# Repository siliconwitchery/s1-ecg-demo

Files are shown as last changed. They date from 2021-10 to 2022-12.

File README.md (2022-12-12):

# S1 ECG Reference Kit

**Features:**

- Single chip frontend based on the [AD8233](https://www.analog.com/en/products/ad8233.html)
- S1 Module with Bluetooth 5.2 and FPGA
- Integrated lithium battery
- Ultra low power auto-sleep down to 175uA
- Open source design

**Applications:**

- Learning and teaching around heart health
- Research of ML based ECG algorithms
- Wireless ECG data logging
- New product development

A powerful analog frontend combined with the S1 Module makes this an all-in-one kit to deploy and test algorithms with ease. Be that for learning, research, or as the starting point for your next product.

<br>

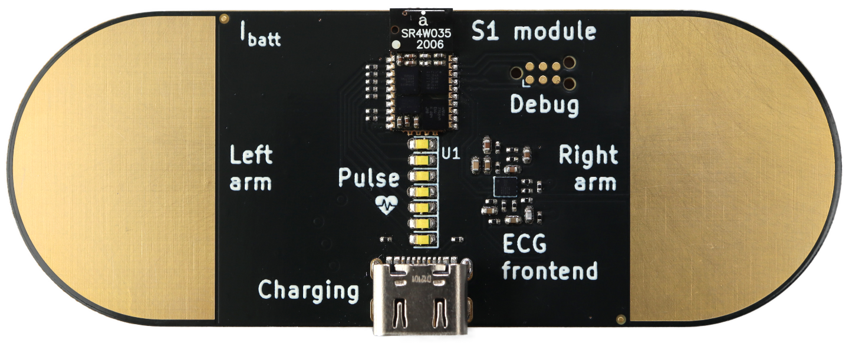
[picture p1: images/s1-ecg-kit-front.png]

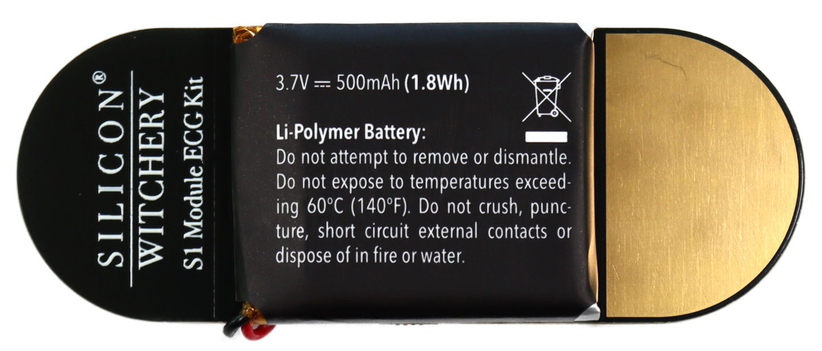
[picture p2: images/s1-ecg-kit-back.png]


<br>

## Get the hardware

**Order the S1 ECG Kit from [Digi-Key](https://www.digikey.com/en/products/detail/silicon-witchery/S1-ECG-KIT/15926538) 🛍**

You're also free to build your own hardware using the design files in this repository. Everything is open source and ready to build upon.

- [Schematic](https://github.com/siliconwitchery/s1-ecg-demo/blob/main/schematic.pdf)
- [Gerber files](https://github.com/siliconwitchery/s1-ecg-demo/tree/main/gerber-files/factory-version)
- [Bill of materials](https://github.com/siliconwitchery/s1-ecg-demo/blob/main/bill-of-materials.pdf)

The design is produced in [KiCad v6.0.1](https://www.kicad.org/download/).

## Building the code

The S1 ECG reference kit uses a three probe measurement to determine heart activity. By holding the board with both hands, the device automatically wakes from sleep, and begins calibrating the amplifier sensitivity. After a few seconds, you will see your pulse displayed on the LED bar graph. Letting go of the terminals puts the system back into sleep mode.

The base firmware is highly expandable and a perfect starting point for new designs. To get started, begin by cloning this repository.

``` bash
git clone --recurse-submodules https://github.com/siliconwitchery/s1-ecg-demo.git
cd s1-ecg-demo
```

If you haven't already, set up these [tools](https://github.com/siliconwitchery/s1-sdk/blob/main/README.md#setting-up-the-tools) in order to build the project.

You should then be able to run `make`. *Be sure to include the path to your NRF SDK folder*.

``` bash
make -C firmware build-verilog NRF_SDK_PATH=${HOME}/nRF5_SDK
make -C firmware flash NRF_SDK_PATH=${HOME}/nRF5_SDK
```

The first `make` command will build the Verilog project, and convert the binary file into a header file. The nRF application transfers this binary to the FPGA after boot up. In your application, you could download this binary dynamically over Bluetooth rather than storing it within the flash of the nRF chip.

The second `make` command builds the nRF code, and flashes the module using a J-Link debugger. You can also use an [nRF52 devkit](https://www.nordicsemi.com/Products/Development-hardware/nrf52-dk), or [JLink Edu Mini](https://www.digikey.se/product-detail/en/segger-microcontroller-systems/8-08-91-J-LINK-EDU-MINI/899-1061-ND/7387472) along with and [this](https://www.tag-connect.com/product/tc2030-ctx-nl-6-pin-no-legs-cable-with-10-pin-micro-connector-for-cortex-processors) 6pin cable to flash your board.

Once you're up and running, you can begin customizing the application to your needs. Be sure to visit our documentation center to learn more about the S1 Module, as well as its features.

## Measuring sleep current

The board features a jumper disconnect to allow for the battery current to be directly measured. During sleep modes, this can be configured down to as low as 175uA or less, depending on the sleep state needed.

Note that if the USB-C power cable is plugged in while measuring, the charge current to the battery will be measured rather than the discharge current.

## Sensitivity of the ECG amplifier and EMI

The ECG amplifier is designed to pick up the tiny signals across your hands. It's therefore quite sensitive to external interference. Operation solely from the lithium battery is ideal. Here the board remains isolated from other noise sources and accurate measurements can be made.

Certain USB-C charges can induce a lot of EMI and ground loops can be created via the users hands. This may create noise in the measurement so it's worth keeping in mind when developing or logging data.

## Looking after the battery

**Lithium batteries are of course dangerous if improperly handled.** The S1 module features safety checks to avoid damage and such damage is unlikely. However it is possible to misconfigure the integrated power management IC to overcharge/undercharge or charge the lithium battery with too much current.

It is recommended to only use the battery configuration provided in this example to ensure safety and lifetime of the lithium battery.

If in doubt, it is possible to simply remove the battery current measurement jumper, and this will disconnect the battery from the system.

## Bugs and improvements

If you have any questions, or if something is unclear, feel free to create an [issue](https://github.com/siliconwitchery/s1-ecg-demo/issues) and we'll try our best to improve it.

## Licence

Copyright 2022 © Silicon Witchery.

This design is licenced under: [CERN Open Hardware Licence Version 2 - Permissive](https://ohwr.org/cern_ohl_p_v2.pdf).

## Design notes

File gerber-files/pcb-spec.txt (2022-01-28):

----------------------------------------------------------------------
                            PCB specifications
----------------------------------------------------------------------
Board type:             HDI
Total Dimension:        80.2 x 30.2 mm
Copper Layers:          4
Material:               TG-150 FR4
Board Thickness:        2mm
Min track / spacing:    3mil / 3mil
Min hole size:          0.3mm
Soldermask Color:       Black
Silkscreen:             White
Surface Finish:         ENIG RoHS
Outside opper Weight:   1oz
Inside opper Weight:    1oz
Plated via in pad:      Yes

-----------------------------------------------------------------------
                            Board Stackup
-----------------------------------------------------------------------
Copper      Layer                           Filename
-----------------------------------------------------------------------
            Front paste                     s1-ecg-demo-F_Paste.gbr
            Front silk                      s1-ecg-demo-F_Silkscreen.gbr
            Front mask                      s1-ecg-demo-F_Mask.gbr
1           Front copper                    s1-ecg-demo-F_Cu.gbr
            Laser drill 1-2                 s1-ecg-demo-front-in1.drl
2           Front inner copper              s1-ecg-demo-In1_Cu.gbr
3           Back inner copper               s1-ecg-demo-In2_Cu.gbr
4           Back copper                     s1-ecg-demo-B_Cu.gbr
            Back mask                       s1-ecg-demo-B_Mask.gbr
            Back silk                       s1-ecg-demo-B_Silkscreen.gbr

            Plated & non-plated drill holes s1-ecg-demo.drl
            Milling                         s1-ecg-demo-Edge_Cuts.gbr

            Component position              s1-ecg-demo-all.pos

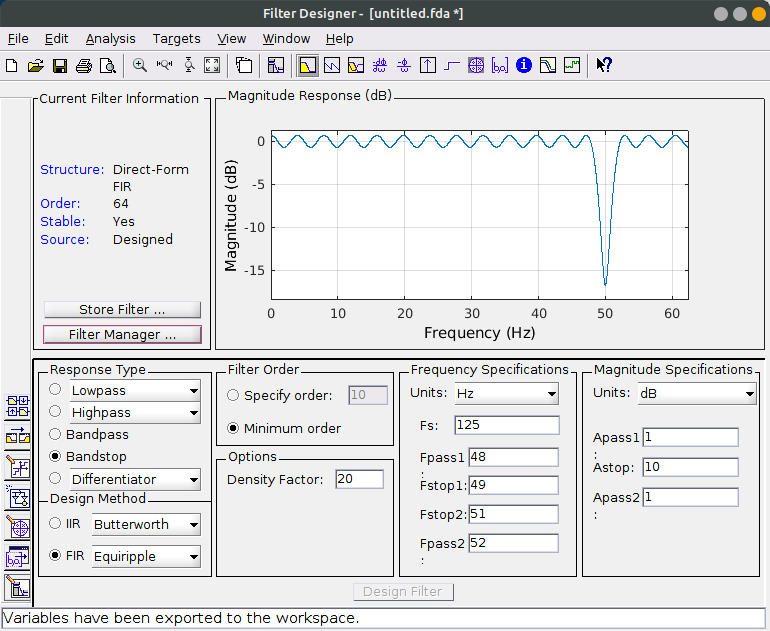
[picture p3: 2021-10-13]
images/fir-filter.png

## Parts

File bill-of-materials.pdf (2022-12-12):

| | | | | Silicon Witchery S1 ECG Kit | Bill of Materials | Main BOM - 12 December 2022
Part Name | Part Number | Vendor | Designator | Footprint | Quantity | Primary Supplier | Assembly Notes
220nF 16V Ceramic Cap | GCM155R71C224KE02D | Murata | C1, C2 | 0402 | 2 | Digikey: 490-10671-1-ND (https://www.digikey.se/product-detail/en/murata-electronics/GCM155R71C224KE02D/490-10671-1-ND/5251434) | -
1uF 6.3V Ceramic Cap | GRM155R70J105KA12J | Murata | C3 | 0402 | 1 | Digikey: 490-13339-1-ND (https://www.digikey.se/product-detail/en/murata-electronics/GRM155R70J105KA12J/490-13339-1-ND/5973350) | -
1nF 50V Ceramic Cap | GRM1555C1H102JA01D | Murata | C4 | 0402 | 1 | Digikey: 490-3244-1-ND (https://www.digikey.se/product-detail/en/murata-electronics/GRM1555C1H102JA01D/490-3244-1-ND/702785) | -
100nF 16V Ceramic Cap | GCM155R71C104KA55D | Murata | C5 | 0402 | 1 | Digikey: 490-4759-1-ND (https://www.digikey.se/product-detail/en/murata-electronics/GCM155R71C104KA55D/490-4759-1-ND/1641678) | -
10uF 6.3V Ceramic Cap | GRM155R60J106ME15D | Murata | C6 | 0402 | 1 | Digikey: 490-13238-1-ND | -
22nF 50V Ceramic Cap | GCM155R71H223KA55D | Murata | C7 | 0402 | 1 | Digikey: 490-4763-1-ND (https://www.digikey.se/product-detail/en/murata-electronics/GCM155R71H223KA55D/490-4763-1-ND/1641682) | -
10nF 50V Ceramic Cap | GCM155R71H103KA55D | Murata | C8 | 0402 | 1 | Digikey: 490-4762-1-ND (https://www.digikey.se/product-detail/en/murata-electronics/GCM155R71H103KA55D/490-4762-1-ND/1641681) | -
0.1” 2-Pin Header | GREC002SBSN-M89RC (https://media.digikey.com/PDF/Data%20Sheets/Sullins%20PDFs/xRxCzzzSxxN-M89RC_11659-B.pdf) | Sullins | J5 | SMD | 1 | Digikey: S1113EC-02-ND (https://www.digikey.se/products/en?keywords=GREC002SBSN-M89RC) | -
USB Type-C Connector | DX07S016JA1R1500 (https://www.mouser.se/datasheet/2/206/JAE_Electronics_01282020_DX07-1729578.pdf) (Drawing) (https://www.jae.com/direct/topics/topics_file_download/topics_id=91780&ext_no=06&index=0&_lang=en&v=2020041313384666992409) | JAE | J6 | SMD | 1 | Mouser: 656-DX07S016JA1R1500 (https://www.mouser.se/ProductDetail/JAE-Electronics/DX07S016JA1R1500) | -
150mAh LiPo Battery | LP402025 | PKCell | J7 | 20x26mm | 1 | Adafruit: 1317 (https://www.adafruit.com/product/1317) | See back silkscreen for polarity
White LED | IN-S63AT5UW (https://www.mouser.se/datasheet/2/180/IN-S63AT_Series_V1.1-1488271.pdf) | Inolux | LED1-LED7 | 0603 | 7 | Mouser: 743-IN-S63AT5UW (https://www.mouser.se/ProductDetail/Inolux/IN-S63AT5UW) | See Front View image for Cathode mark
S1 Module | S1-MOD | Silicon Witchery | MOD1 | SMD | 1 | Silicon Witchery | See Front View image for Pin 1 location
182k Film Resistor | RC0201FR-07182KL | Yageo | R2, R4 | 0201 | 2 | Digikey: YAG2451CT-ND (https://www.digikey.se/product-detail/en/yageo/RC0201FR-07182KL/YAG2451CT-ND/5281315) | -
10M Film Resistor | RC0201JR-0710ML | Yageo | R1, R3, R5-R8 | 0201 | 6 | Digikey: YAG2861CT-ND (https://www.digikey.se/product-detail/en/yageo/RC0201JR-0710ML/YAG2861CT-ND/5281725) | -
499k Film Resistor | RC0201FR-07499KL | Yageo | R9 | 0201 | 1 | Digikey: YAG2699CT-ND (https://www.digikey.se/product-detail/en/yageo/RC0201FR-07499KL/YAG2699CT-ND/5281563) | -
200k Film Resistor | RC0201FR-07200KL | Yageo | R10 | 0201 | 1 | Digikey: YAG2275CT-ND (https://www.digikey.se/product-detail/en/yageo/RC0201FR-07200KL/YAG2275CT-ND/5252389) | -
100k Film Resistor | RC0201JR-07100KL | Yageo | R12, R13 | 0201 | 2 | Digikey: 311-100KNCT-ND (https://www.digikey.se/product-detail/en/yageo/RC0201JR-07100KL/311-100KNCT-ND/1949005)
1M Film Resistor | RC0201FR-071ML | Yageo | R11, R14 | 0201 | 2 | Digikey: 311-1MMCT-ND (https://www.digikey.se/product-detail/en/yageo/RC0201FR-071ML/311-1MMCT-ND/4340582) | -
5.1k Film Resistor | RC0201FR-075K1L | Yageo | R15, R16 | 0201 | 2 | Digikey: YAG2741CT-ND (https://www.digikey.se/product-detail/en/yageo/RC0201FR-075K1L/YAG2741CT-ND/5281605) | -
655R Film Resistor | RC0201FR-07649RL | Yageo | R17-R23 | 0201 | 7 | Digikey: YAG2761CT-ND (https://www.digikey.se/product-detail/en/yageo/RC0201FR-07649RL/YAG2761CT-ND/5281625) | -
ECG Amplifier IC | AD8233ACBZ-R7 (https://www.analog.com/media/en/technical-documentation/data-sheets/ad8233.pdf) | Analog Devices | U1 | WLCSP-20 | 1 | Digikey: AD8233ACBZ-R7CT-ND (https://www.digikey.se/product-detail/en/AD8233ACBZ-R7/AD8233ACBZ-R7CT-ND/6165553?itemSeq=375386878) | See Front View image for Pin 1 location
0.1” Jumper | QPC02SXGN-RC (https://s3.amazonaws.com/catalogspreads-pdf/PAGE128-129%20.100%20JUMPER.pdf) | Sullins | - | - | 1 | Digikey: S9337-ND (https://www.digikey.se/product-detail/en/sullins-connector-solutions/QPC02SXGN-RC/S9337-ND/2618262) | Goes on J5
PCB | - | - | - | - | 1 | - | -
Total Unique Parts | - | - | - | - | 22 | - | -
Total Parts | - | - | - | - | 42 | -

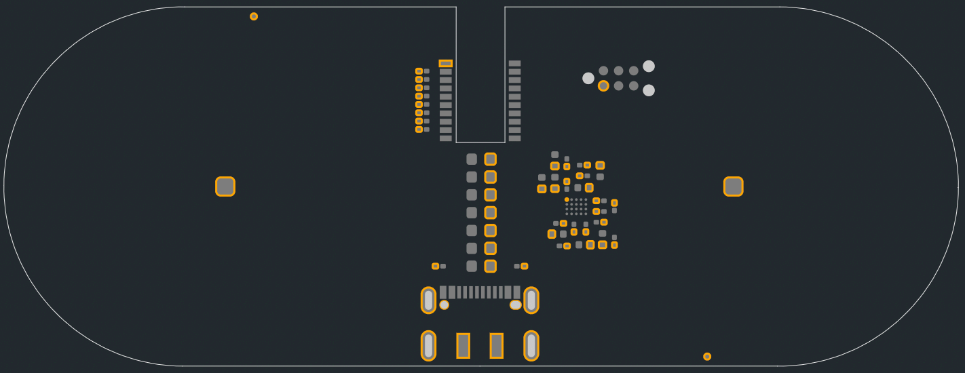
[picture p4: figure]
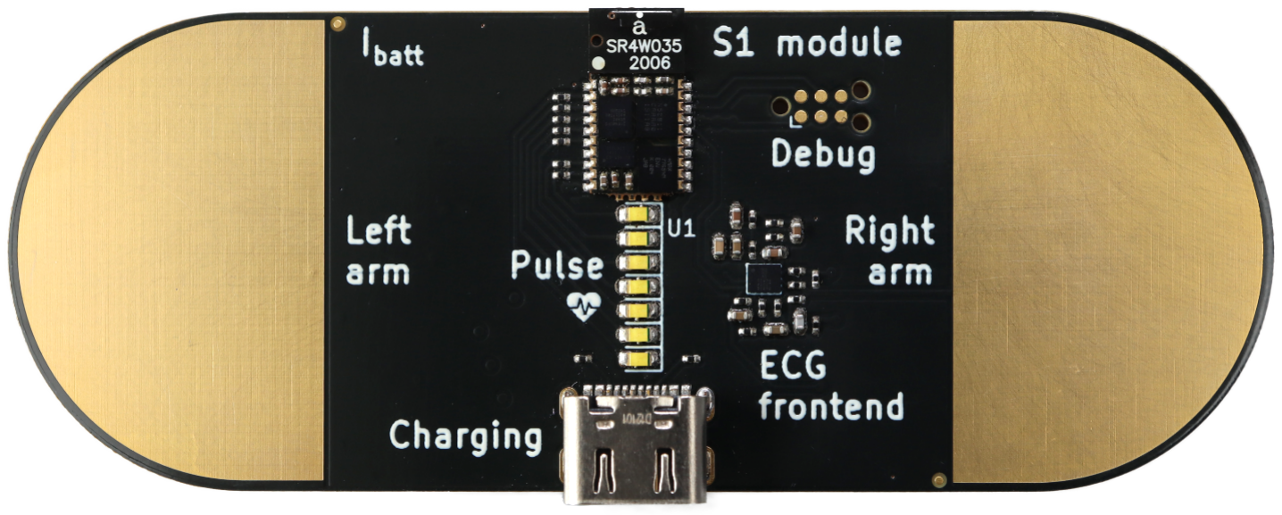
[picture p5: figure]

Front View with Pin 1 highlighted | Reference image

Copyright 2022 © Silicon Witchery.

This design is licensed under CERN OHL-P v2. (https://ohwr.org/cern_ohl_p_v2.pdf)

The design is provided as a demonstration, and has not been or approved for life sustaining or other applications where failure may cause harm to human life, health or damage to property and equipment. Additionally, it has not been designed according to any standards in order to guarantee performance or accuracy. No responsibility is assumed by Silicon Witchery for its use, nor for any infringements of patents or other rights of third parties that may result from its use. These specifications are subject to change without notice.

1

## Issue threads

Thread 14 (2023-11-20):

### ISSUE TITLE
ECG Kit - serial data out 

### ISSUE THREAD

**Issue by stanleyoz** [siliconwitchery/s1-ecg-demo#14]
Hi,
We got hold of the S1 ECG Kit from DigiKey, nice .. it blinks LEDs as per heart-beat and pretty stable. Is there a way to code the board so that it can output serially the amplitude of the waveform so we can ingress the data into our gateway via USB etc? It seems the S1 module does not have any data connection out thru the USB-C connector. 
Please advise. 
Thanks.

**Comment by siliconwitch** [comment]
Hello there! Glad to have the board in your hands 🙂

The most simplest option could be to solder a USB to UART dongle to one of the exposed D1/2/3/4 pads on the back of the board. You'd then need to reprogram the nRF and FPGA to pass through UART data to those pins rather than the LED PWM.

Alternatively, you can connect up the onboard USB jack to D1/D2. You'd need to add little wires very carefully to the jack, and then add the relevant USB IP to the FPGA. It's a lot more work, but would give you the most flexibility.

If instead you want to avoid soldering altogether, you could use our [MicroPython](https://docs.siliconwitchery.com/micropython/micropython/) firmware instead. This would let you stream the data to your gateway over Bluetooth (assuming you have the possibility to add that). You'd do this by executing a script that polls the ADC, and then prints the values back to the host. If you wanted to, you could do all kinds of filtering or preprocessing of the samples before sending them over. To send these samples back, you'd simply use the Python `print()` statement. Our MicroPython firmware essentially just turns the S1 into a remote shell that runs over Bluetooth. Check out the [ADC API](https://docs.siliconwitchery.com/micropython/adc/) to see how this would be done.

For all of these options, you'll need to reprogram the ECG kit. You'll need a [TC2030-CTX-NL](https://www.tag-connect.com/product/tc2030-ctx-nl-6-pin-no-legs-cable-with-10-pin-micro-connector-for-cortex-processors) from Tag-Connect, as well as a J-Link programmer. You can also use an nRF52DK board as shown [here](https://docs.siliconwitchery.com/s1-module/s1-module/#programming-the-nrf52).

Hope this helps!

**Comment by stanleyoz** [comment]
Possible solutions ... but can you contact me at stanley"at"amplified.com.au? Due to proprietary nature of this gov medical project, prefer to share more details off the github. Thanks.

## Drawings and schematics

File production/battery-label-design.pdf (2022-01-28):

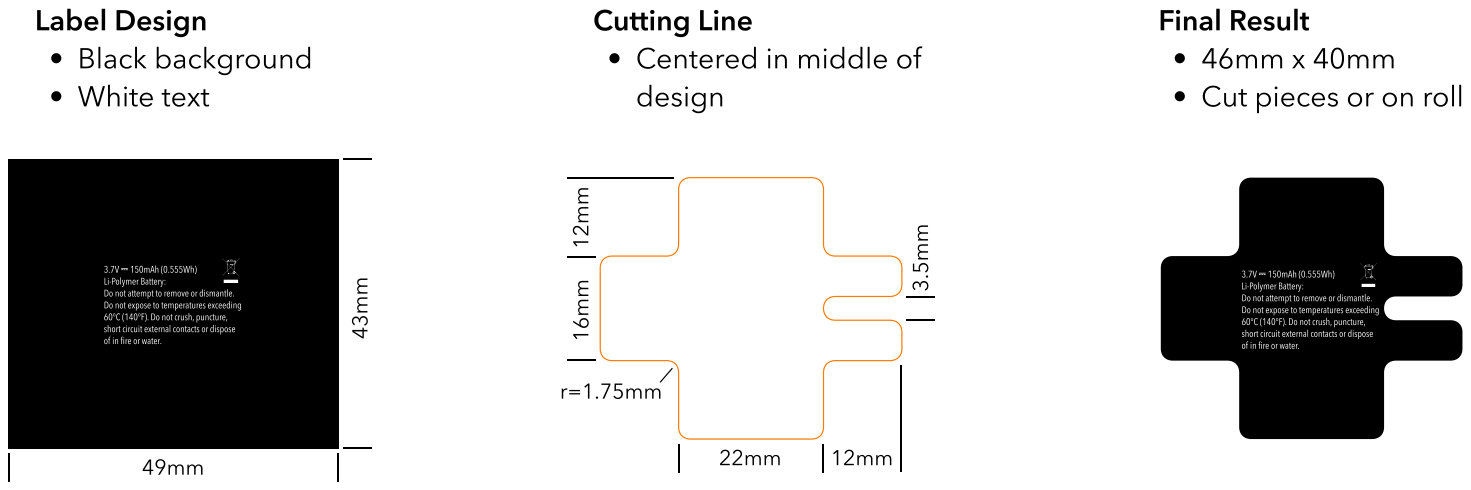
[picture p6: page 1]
Label Desig  Black backgroun  White text

Cutting Lins
 Centered in middle of
design
r=1.75mm ¹²mm

Final Resul
 Cut pieces or on roll

3.7V ⎓ 150mAh (0.555Wh)
Li-Polymer Battery:
Do not attempt to remove or dismantle.
Do not expose to temperatures exceeding
60°C (140°F). Do not crush, puncture,
short circuit external contacts or dispose
of in fire or water.

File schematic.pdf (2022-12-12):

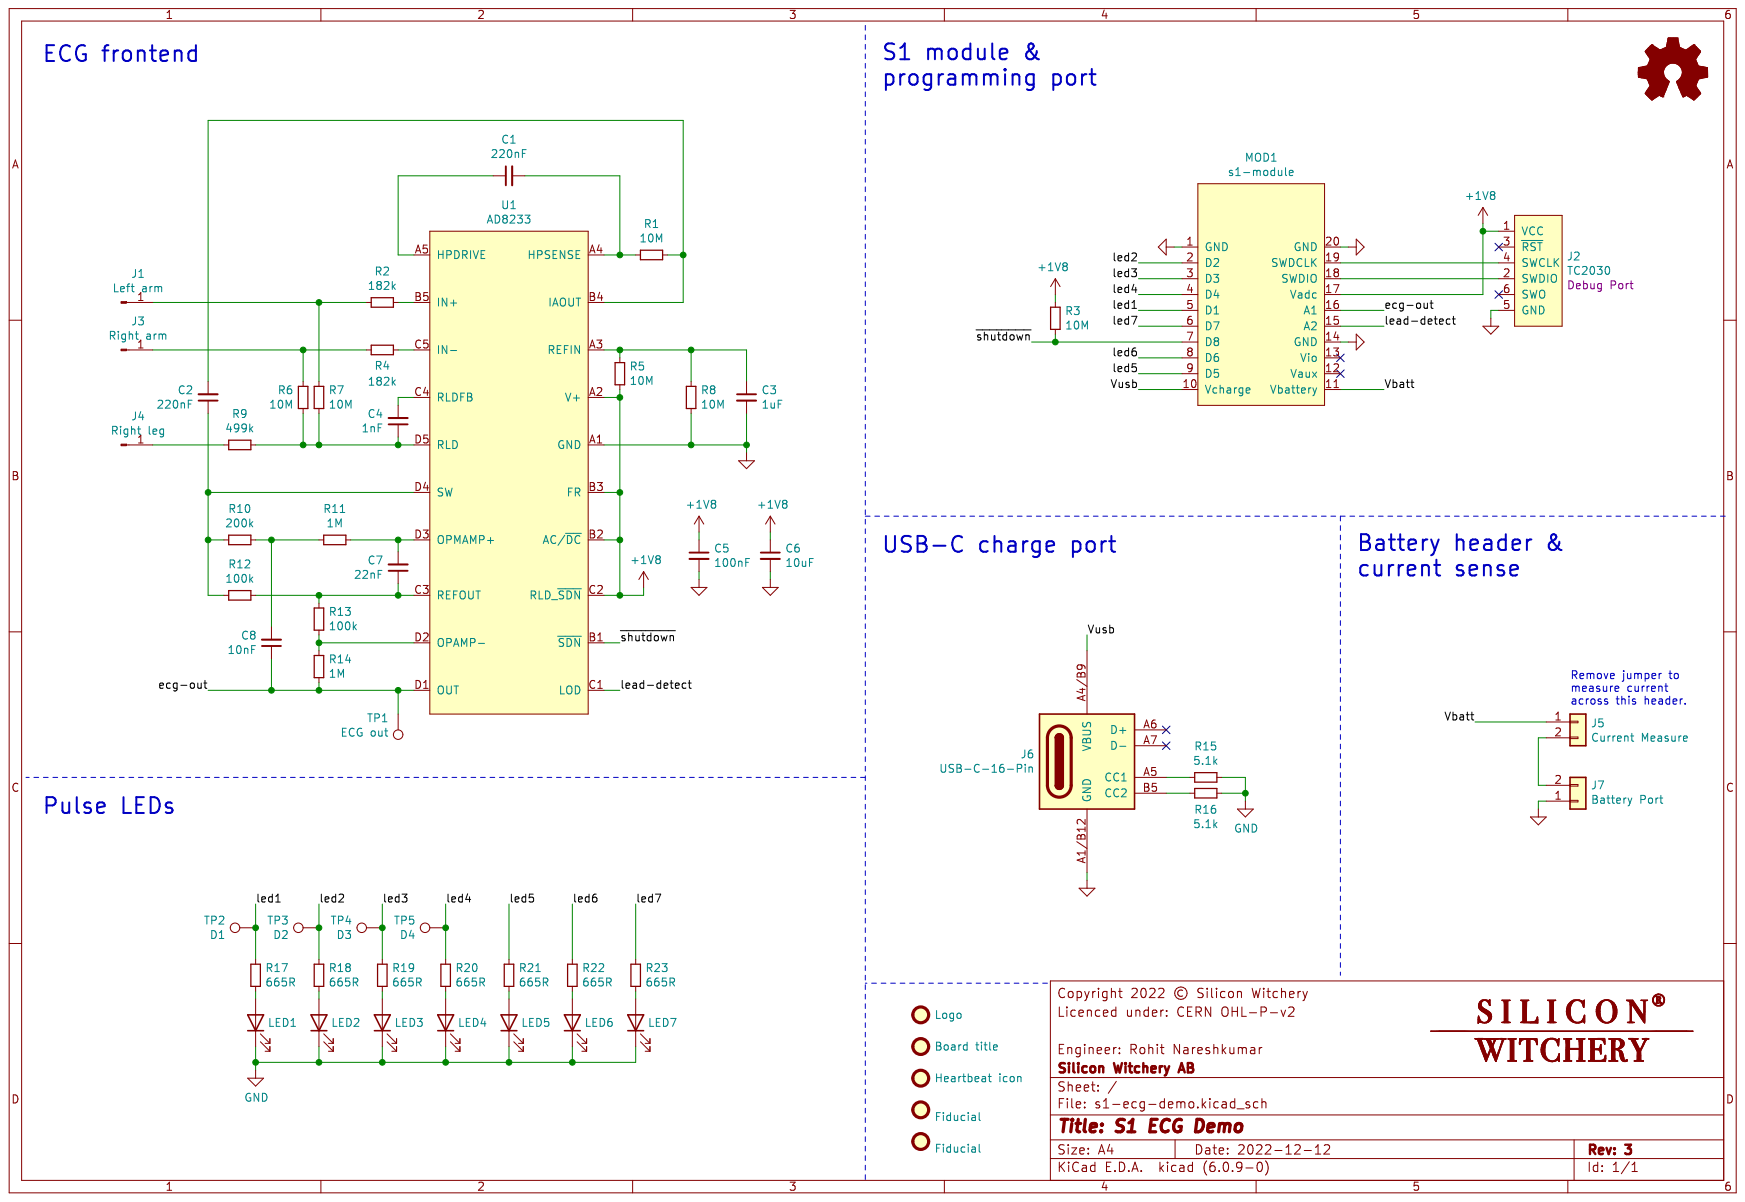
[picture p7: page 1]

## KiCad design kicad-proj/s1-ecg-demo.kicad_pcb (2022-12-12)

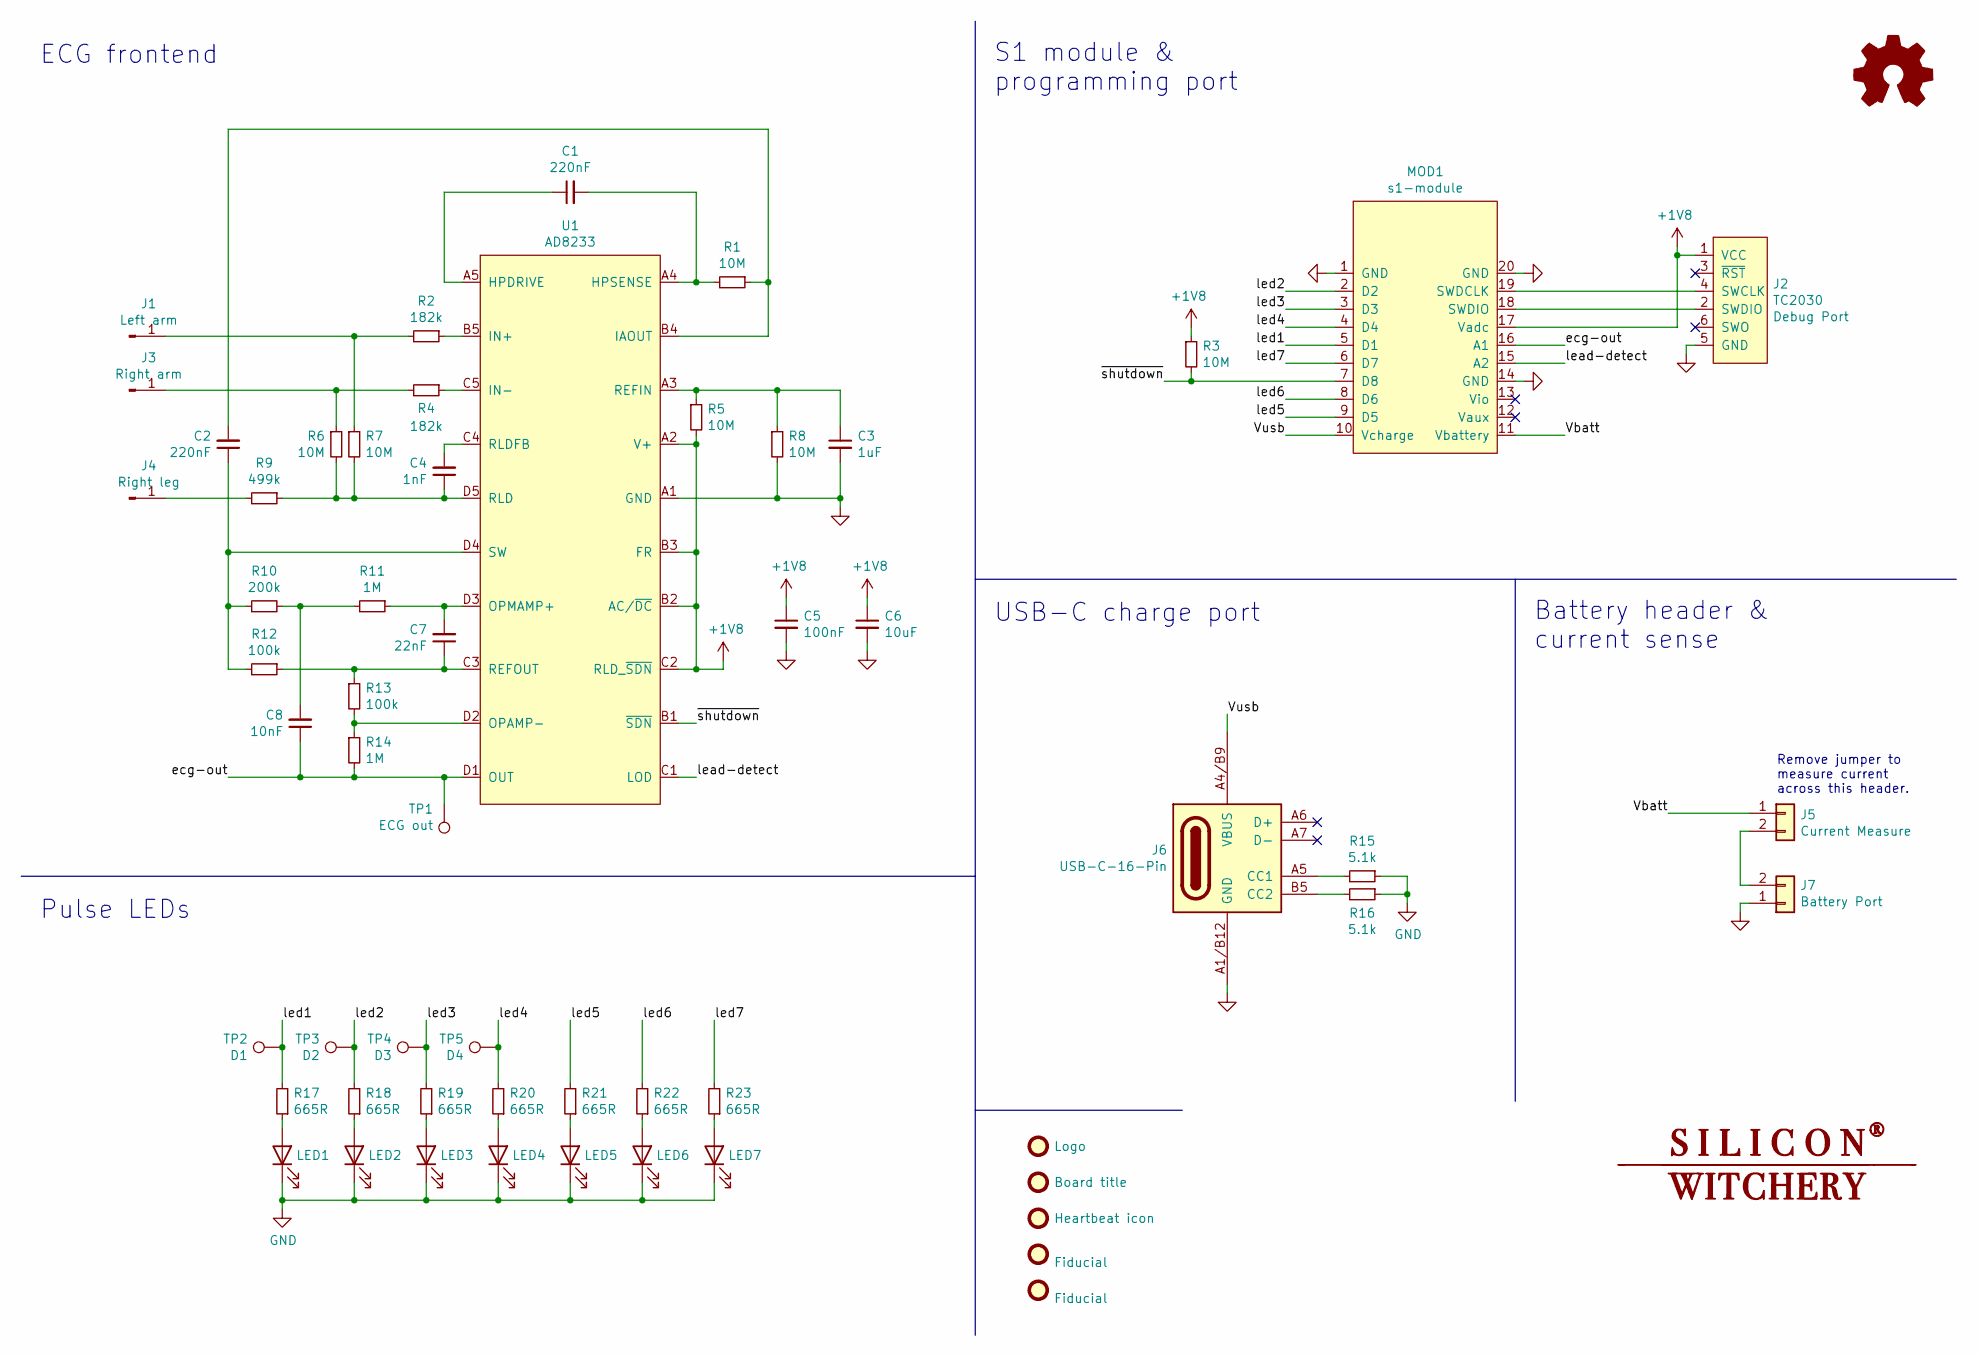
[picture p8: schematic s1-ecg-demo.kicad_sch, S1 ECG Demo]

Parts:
C1, C2: 220nF; C_0402_1005Metric
C3: 1uF; C_0402_1005Metric
C4: 1nF; C_0402_1005Metric
C5: 100nF; C_0402_1005Metric
C6: 10uF; C_0402_1005Metric
C7: 22nF; C_0402_1005Metric
C8: 10nF; C_0402_1005Metric
FID1: Logo; sw-logo
FID2: Board title; title
FID3: Heartbeat icon; heartbeat
FID4, FID5: Fiducial; Fiducial_0.5mm_Mask1mm
J1: Left arm; ECG-pad
J2: TC2030; Tag-Connect_TC2030-IDC-NL_2x03_P1.27mm_Vertical
J3: Right arm; ECG-pad
J4: Right leg; ECG-pad
J5: Current Measure; Conn_2_SMD_2.54mm
J6: USB-C-16-Pin; DX07S016JA1R1500
J7: Battery Port; Conn_2_SMD_2.54mm
LED1, LED2, LED3, LED4, LED5, LED6, LED7: LED; LED_0603_1608Metric
MOD1: s1-module
R1, R3, R5, R6, R7, R8: 10M; R_0201_0603Metric
R2, R4: 182k; R_0201_0603Metric
R9: 499k; R_0201_0603Metric
R10: 200k; R_0201_0603Metric
R11, R14: 1M; R_0201_0603Metric
R12, R13: 100k; R_0201_0603Metric
R15, R16: 5.1k; R_0201_0603Metric
R17, R18, R19, R20, R21, R22, R23: 665R; R_0201_0603Metric
TP1: ECG out; TestPoint_Pad_D1.0mm
TP2: D1; TestPoint_Pad_D1.0mm
TP3: D2; TestPoint_Pad_D1.0mm
TP4: D3; TestPoint_Pad_D1.0mm
TP5: D4; TestPoint_Pad_D1.0mm
U1: AD8233; WLCSP-20

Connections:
+1V8: C5.1, C6.1, J2.1 (VCC), MOD1.17 (Vadc), R3.1, R5.2, U1.A2 (V+), U1.B2 (AC/~DC), U1.B3 (FR), U1.C2 (RLD_~SDN)
/Vbatt: J5.1, MOD1.11 (Vbattery)
/ecg-out: C8.1, MOD1.16 (A1), R14.2, TP1.1, U1.D1 (OUT)
/lead-detect: MOD1.15 (A2), U1.C1 (LOD)
/led1: MOD1.5 (D1), R17.2, TP2.1
/led2: MOD1.2 (D2), R18.2, TP3.1
/led3: MOD1.3 (D3), R19.2, TP4.1
/led4: MOD1.4 (D4), R20.2, TP5.1
/led5: MOD1.9 (D5), R21.2
/led6: MOD1.8 (D6), R22.2
/led7: MOD1.6 (D7), R23.2
/~shutdown: MOD1.7 (D8), R3.2, U1.B1 (~SDN)
GND: C3.2, C5.2, C6.2, J2.5 (GND), J6.A1/B12 (GND), J6.A12/B1 (GND), J7.1, LED1.1 (K), LED2.1 (K), LED3.1 (K), LED4.1 (K), LED5.1 (K), LED6.1 (K), LED7.1 (K), MOD1.1 (GND), MOD1.14 (GND), MOD1.20 (GND), R8.2, R15.1, R16.1, U1.A1 (GND)
unnamed: C1.1, U1.A5 (HPDRIVE)
unnamed: C1.2, R1.2, U1.A4 (HPSENSE)
unnamed: C2.1, R10.1, R12.2, U1.D4 (SW)
unnamed: C2.2, R1.1, U1.B4 (IAOUT)
unnamed: C3.1, R5.1, R8.1, U1.A3 (REFIN)
unnamed: C4.1, R6.2, R7.2, R9.1, U1.D5 (RLD)
unnamed: C4.2, U1.C4 (RLDFB)
unnamed: C7.1, R12.1, R13.1, U1.C3 (REFOUT)
unnamed: C7.2, R11.1, U1.D3 (OPMAMP+)
unnamed: C8.2, R10.2, R11.2
unnamed: J1.1, R2.2, R7.1
unnamed: J2.2 (SWDIO), MOD1.18 (SWDIO)
unnamed: J2.4 (SWCLK), MOD1.19 (SWDCLK)
unnamed: J3.1, R4.2, R6.1
unnamed: J4.1, R9.2
unnamed: J5.2, J7.2
unnamed: J6.A5 (CC1), R15.2
unnamed: J6.B5 (CC2), R16.2
unnamed: LED1.2 (A), R17.1
unnamed: LED2.2 (A), R18.1
unnamed: LED3.2 (A), R19.1
unnamed: LED4.2 (A), R20.1
unnamed: LED5.2 (A), R21.1
unnamed: LED6.2 (A), R22.1
unnamed: LED7.2 (A), R23.1
unnamed: R2.1, U1.B5 (IN+)
unnamed: R4.1, U1.C5 (IN-)
unnamed: R13.2, R14.1, U1.D2 (OPAMP-)
VBUS: J6.A4/B9 (VBUS), J6.A9/B4 (VBUS), MOD1.10 (Vcharge)

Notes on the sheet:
Battery header & current sense
USB-C charge port
S1 module & programming port
ECG frontend
Remove jumper to measure current across this header.
Pulse LEDs

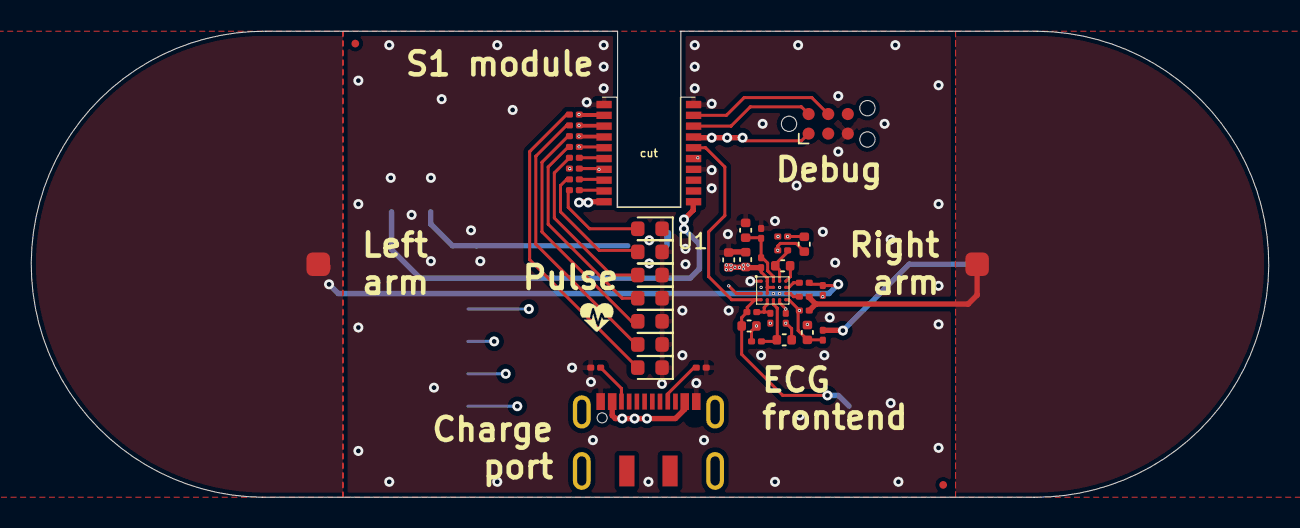
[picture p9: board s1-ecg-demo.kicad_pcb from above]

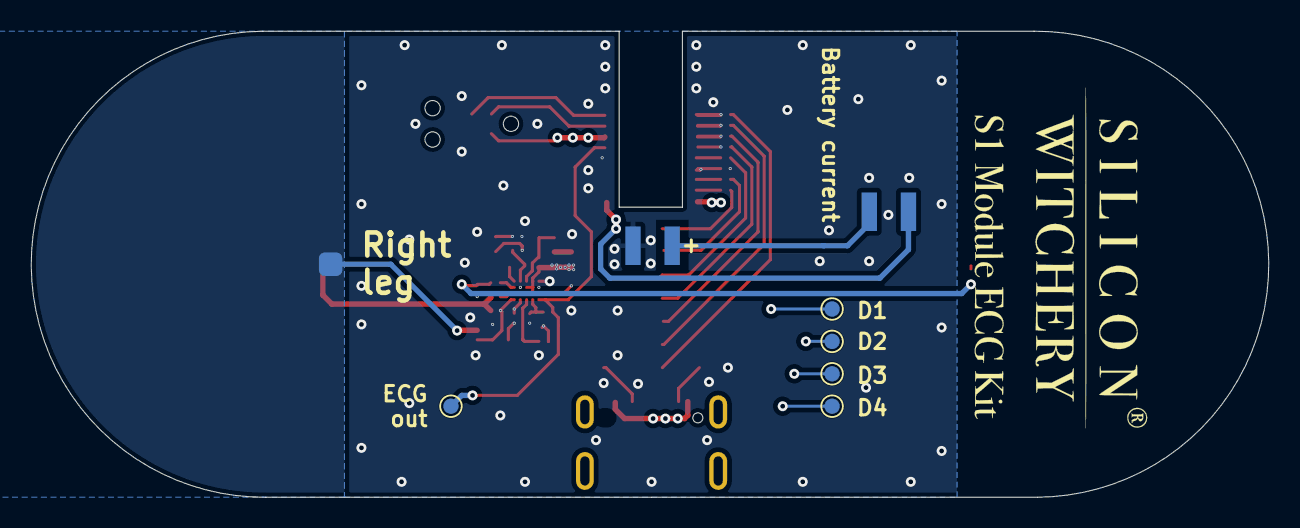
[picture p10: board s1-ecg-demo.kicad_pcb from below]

Board: 4 copper layers, 80.2 x 30.2 mm, 57 parts (10 on the bottom side), 42 nets.

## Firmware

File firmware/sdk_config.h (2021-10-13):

/**
 * Copyright (c) 2017 - 2020, Nordic Semiconductor ASA
 *
 * All rights reserved.
 *
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
 * 3. Neither the name of Nordic Semiconductor ASA nor the names of its
 *    contributors may be used to endorse or promote products derived from this
 *    software without specific prior written permission.
 *
 * 4. This software, with or without modification, must only be used with a
 *    Nordic Semiconductor ASA integrated circuit.
 *
 * 5. Any software provided in binary form under this license must not be reverse
 *    engineered, decompiled, modified and/or disassembled.
 *
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
 */

#ifndef SDK_CONFIG_H
#define SDK_CONFIG_H
// <<< Use Configuration Wizard in Context Menu >>>\n
#ifdef USE_APP_CONFIG
#include "app_config.h"
#endif

//==========================================================

// <h> nRF_Core

//==========================================================
// <e> NRF_MPU_LIB_ENABLED - nrf_mpu_lib - Module for MPU
//==========================================================
#ifndef NRF_MPU_LIB_ENABLED
#define NRF_MPU_LIB_ENABLED 0
#endif
// <q> NRF_MPU_LIB_CLI_CMDS  - Enable CLI commands specific to the module.

#ifndef NRF_MPU_LIB_CLI_CMDS
#define NRF_MPU_LIB_CLI_CMDS 0
#endif

// </e>

// <e> NRF_STACK_GUARD_ENABLED - nrf_stack_guard - Stack guard
//==========================================================
#ifndef NRF_STACK_GUARD_ENABLED
#define NRF_STACK_GUARD_ENABLED 0
#endif
// <o> NRF_STACK_GUARD_CONFIG_SIZE  - Size of the stack guard.

// <5=> 32 bytes
// <6=> 64 bytes
// <7=> 128 bytes
// <8=> 256 bytes
// <9=> 512 bytes
// <10=> 1024 bytes
// <11=> 2048 bytes
// <12=> 4096 bytes

#ifndef NRF_STACK_GUARD_CONFIG_SIZE
#define NRF_STACK_GUARD_CONFIG_SIZE 7
#endif

// </e>

// </h>
//==========================================================

// <h> nRF_Crypto

//==========================================================
// <e> NRF_CRYPTO_ENABLED - nrf_crypto - Cryptography library.
//==========================================================
#ifndef NRF_CRYPTO_ENABLED
#define NRF_CRYPTO_ENABLED 0
#endif
// <o> NRF_CRYPTO_ALLOCATOR  - Memory allocator

// <i> Choose memory allocator used by nrf_crypto. Default is alloca if possible or nrf_malloc otherwise. If 'User macros' are selected, the user has to create 'nrf_crypto_allocator.h' file that contains NRF_CRYPTO_ALLOC, NRF_CRYPTO_FREE, and NRF_CRYPTO_ALLOC_ON_STACK.
// <0=> Default
// <1=> User macros
// <2=> On stack (alloca)
// <3=> C dynamic memory (malloc)
// <4=> SDK Memory Manager (nrf_malloc)

#ifndef NRF_CRYPTO_ALLOCATOR
#define NRF_CRYPTO_ALLOCATOR 0
#endif

// <e> NRF_CRYPTO_BACKEND_CC310_BL_ENABLED - Enable the ARM Cryptocell CC310 reduced backend.

// <i> The CC310 hardware-accelerated cryptography backend with reduced functionality and footprint (only available on nRF52840).
//==========================================================
#ifndef NRF_CRYPTO_BACKEND_CC310_BL_ENABLED
#define NRF_CRYPTO_BACKEND_CC310_BL_ENABLED 0
#endif
// <q> NRF_CRYPTO_BACKEND_CC310_BL_ECC_SECP224R1_ENABLED  - Enable the secp224r1 elliptic curve support using CC310_BL.

#ifndef NRF_CRYPTO_BACKEND_CC310_BL_ECC_SECP224R1_ENABLED
#define NRF_CRYPTO_BACKEND_CC310_BL_ECC_SECP224R1_ENABLED 0
#endif

// <q> NRF_CRYPTO_BACKEND_CC310_BL_ECC_SECP256R1_ENABLED  - Enable the secp256r1 elliptic curve support using CC310_BL.

#ifndef NRF_CRYPTO_BACKEND_CC310_BL_ECC_SECP256R1_ENABLED
#define NRF_CRYPTO_BACKEND_CC310_BL_ECC_SECP256R1_ENABLED 1
#endif

// <q> NRF_CRYPTO_BACKEND_CC310_BL_HASH_SHA256_ENABLED  - CC310_BL SHA-256 hash functionality.

// <i> CC310_BL backend implementation for hardware-accelerated SHA-256.

#ifndef NRF_CRYPTO_BACKEND_CC310_BL_HASH_SHA256_ENABLED
#define NRF_CRYPTO_BACKEND_CC310_BL_HASH_SHA256_ENABLED 1
#endif

// <q> NRF_CRYPTO_BACKEND_CC310_BL_HASH_AUTOMATIC_RAM_BUFFER_ENABLED  - nrf_cc310_bl buffers to RAM before running hash operation

// <i> Enabling this makes hashing of addresses in FLASH range possible. Size of buffer allocated for hashing is set by NRF_CRYPTO_BACKEND_CC310_BL_HASH_AUTOMATIC_RAM_BUFFER_SIZE

#ifndef NRF_CRYPTO_BACKEND_CC310_BL_HASH_AUTOMATIC_RAM_BUFFER_ENABLED
#define NRF_CRYPTO_BACKEND_CC310_BL_HASH_AUTOMATIC_RAM_BUFFER_ENABLED 0
#endif

// <o> NRF_CRYPTO_BACKEND_CC310_BL_HASH_AUTOMATIC_RAM_BUFFER_SIZE - nrf_cc310_bl hash outputs digests in little endian
// <i> Makes the nrf_cc310_bl hash functions output digests in little endian format. Only for use in nRF SDK DFU!

#ifndef NRF_CRYPTO_BACKEND_CC310_BL_HASH_AUTOMATIC_RAM_BUFFER_SIZE
#define NRF_CRYPTO_BACKEND_CC310_BL_HASH_AUTOMATIC_RAM_BUFFER_SIZE 4096
#endif

// <q> NRF_CRYPTO_BACKEND_CC310_BL_INTERRUPTS_ENABLED  - Enable Interrupts while support using CC310 bl.

// <i> Select a library version compatible with the configuration. When interrupts are disable, a version named _noint must be used

#ifndef NRF_CRYPTO_BACKEND_CC310_BL_INTERRUPTS_ENABLED
#define NRF_CRYPTO_BACKEND_CC310_BL_INTERRUPTS_ENABLED 1
#endif

// </e>

// <e> NRF_CRYPTO_BACKEND_CC310_ENABLED - Enable the ARM Cryptocell CC310 backend.

// <i> The CC310 hardware-accelerated cryptography backend (only available on nRF52840).
//==========================================================
#ifndef NRF_CRYPTO_BACKEND_CC310_ENABLED
#define NRF_CRYPTO_BACKEND_CC310_ENABLED 0
#endif
// <q> NRF_CRYPTO_BACKEND_CC310_AES_CBC_ENABLED  - Enable the AES CBC mode using CC310.

#ifndef NRF_CRYPTO_BACKEND_CC310_AES_CBC_ENABLED
#define NRF_CRYPTO_BACKEND_CC310_AES_CBC_ENABLED 1
#endif

// <q> NRF_CRYPTO_BACKEND_CC310_AES_CTR_ENABLED  - Enable the AES CTR mode using CC310.

#ifndef NRF_CRYPTO_BACKEND_CC310_AES_CTR_ENABLED
#define NRF_CRYPTO_BACKEND_CC310_AES_CTR_ENABLED 1
#endif

// <q> NRF_CRYPTO_BACKEND_CC310_AES_ECB_ENABLED  - Enable the AES ECB mode using CC310.

#ifndef NRF_CRYPTO_BACKEND_CC310_AES_ECB_ENABLED
#define NRF_CRYPTO_BACKEND_CC310_AES_ECB_ENABLED 1
#endif

// <q> NRF_CRYPTO_BACKEND_CC310_AES_CBC_MAC_ENABLED  - Enable the AES CBC_MAC mode using CC310.

#ifndef NRF_CRYPTO_BACKEND_CC310_AES_CBC_MAC_ENABLED
#define NRF_CRYPTO_BACKEND_CC310_AES_CBC_MAC_ENABLED 1
#endif

// <q> NRF_CRYPTO_BACKEND_CC310_AES_CMAC_ENABLED  - Enable the AES CMAC mode using CC310.

#ifndef NRF_CRYPTO_BACKEND_CC310_AES_CMAC_ENABLED
#define NRF_CRYPTO_BACKEND_CC310_AES_CMAC_ENABLED 1
#endif

// <q> NRF_CRYPTO_BACKEND_CC310_AES_CCM_ENABLED  - Enable the AES CCM mode using CC310.

#ifndef NRF_CRYPTO_BACKEND_CC310_AES_CCM_ENABLED
#define NRF_CRYPTO_BACKEND_CC310_AES_CCM_ENABLED 1
#endif

// <q> NRF_CRYPTO_BACKEND_CC310_AES_CCM_STAR_ENABLED  - Enable the AES CCM* mode using CC310.

#ifndef NRF_CRYPTO_BACKEND_CC310_AES_CCM_STAR_ENABLED
#define NRF_CRYPTO_BACKEND_CC310_AES_CCM_STAR_ENABLED 1
#endif

// <q> NRF_CRYPTO_BACKEND_CC310_CHACHA_POLY_ENABLED  - Enable the CHACHA-POLY mode using CC310.

#ifndef NRF_CRYPTO_BACKEND_CC310_CHACHA_POLY_ENABLED
#define NRF_CRYPTO_BACKEND_CC310_CHACHA_POLY_ENABLED 1
#endif

// <q> NRF_CRYPTO_BACKEND_CC310_ECC_SECP160R1_ENABLED  - Enable the secp160r1 elliptic curve support using CC310.

#ifndef NRF_CRYPTO_BACKEND_CC310_ECC_SECP160R1_ENABLED
#define NRF_CRYPTO_BACKEND_CC310_ECC_SECP160R1_ENABLED 1
#endif

// <q> NRF_CRYPTO_BACKEND_CC310_ECC_SECP160R2_ENABLED  - Enable the secp160r2 elliptic curve support using CC310.

#ifndef NRF_CRYPTO_BACKEND_CC310_ECC_SECP160R2_ENABLED
#define NRF_CRYPTO_BACKEND_CC310_ECC_SECP160R2_ENABLED 1
#endif

// <q> NRF_CRYPTO_BACKEND_CC310_ECC_SECP192R1_ENABLED  - Enable the secp192r1 elliptic curve support using CC310.

#ifndef NRF_CRYPTO_BACKEND_CC310_ECC_SECP192R1_ENABLED
#define NRF_CRYPTO_BACKEND_CC310_ECC_SECP192R1_ENABLED 1
#endif

// <q> NRF_CRYPTO_BACKEND_CC310_ECC_SECP224R1_ENABLED  - Enable the secp224r1 elliptic curve support using CC310.

#ifndef NRF_CRYPTO_BACKEND_CC310_ECC_SECP224R1_ENABLED
#define NRF_CRYPTO_BACKEND_CC310_ECC_SECP224R1_ENABLED 1
#endif

// <q> NRF_CRYPTO_BACKEND_CC310_ECC_SECP256R1_ENABLED  - Enable the secp256r1 elliptic curve support using CC310.

#ifndef NRF_CRYPTO_BACKEND_CC310_ECC_SECP256R1_ENABLED
#define NRF_CRYPTO_BACKEND_CC310_ECC_SECP256R1_ENABLED 1
#endif

// <q> NRF_CRYPTO_BACKEND_CC310_ECC_SECP384R1_ENABLED  - Enable the secp384r1 elliptic curve support using CC310.

#ifndef NRF_CRYPTO_BACKEND_CC310_ECC_SECP384R1_ENABLED
#define NRF_CRYPTO_BACKEND_CC310_ECC_SECP384R1_ENABLED 1
#endif

// <q> NRF_CRYPTO_BACKEND_CC310_ECC_SECP521R1_ENABLED  - Enable the secp521r1 elliptic curve support using CC310.

#ifndef NRF_CRYPTO_BACKEND_CC310_ECC_SECP521R1_ENABLED
#define NRF_CRYPTO_BACKEND_CC310_ECC_SECP521R1_ENABLED 1
#endif

// <q> NRF_CRYPTO_BACKEND_CC310_ECC_SECP160K1_ENABLED  - Enable the secp160k1 elliptic curve support using CC310.

#ifndef NRF_CRYPTO_BACKEND_CC310_ECC_SECP160K1_ENABLED
#define NRF_CRYPTO_BACKEND_CC310_ECC_SECP160K1_ENABLED 1
#endif

// <q> NRF_CRYPTO_BACKEND_CC310_ECC_SECP192K1_ENABLED  - Enable the secp192k1 elliptic curve support using CC310.

#ifndef NRF_CRYPTO_BACKEND_CC310_ECC_SECP192K1_ENABLED
#define NRF_CRYPTO_BACKEND_CC310_ECC_SECP192K1_ENABLED 1
#endif

// <q> NRF_CRYPTO_BACKEND_CC310_ECC_SECP224K1_ENABLED  - Enable the secp224k1 elliptic curve support using CC310.

#ifndef NRF_CRYPTO_BACKEND_CC310_ECC_SECP224K1_ENABLED
#define NRF_CRYPTO_BACKEND_CC310_ECC_SECP224K1_ENABLED 1
#endif

// <q> NRF_CRYPTO_BACKEND_CC310_ECC_SECP256K1_ENABLED  - Enable the secp256k1 elliptic curve support using CC310.

#ifndef NRF_CRYPTO_BACKEND_CC310_ECC_SECP256K1_ENABLED
#define NRF_CRYPTO_BACKEND_CC310_ECC_SECP256K1_ENABLED 1
#endif

// <q> NRF_CRYPTO_BACKEND_CC310_ECC_CURVE25519_ENABLED  - Enable the Curve25519 curve support using CC310.

#ifndef NRF_CRYPTO_BACKEND_CC310_ECC_CURVE25519_ENABLED
#define NRF_CRYPTO_BACKEND_CC310_ECC_CURVE25519_ENABLED 1
#endif

// <q> NRF_CRYPTO_BACKEND_CC310_ECC_ED25519_ENABLED  - Enable the Ed25519 curve support using CC310.

#ifndef NRF_CRYPTO_BACKEND_CC310_ECC_ED25519_ENABLED
#define NRF_CRYPTO_BACKEND_CC310_ECC_ED25519_ENABLED 1
#endif

// <q> NRF_CRYPTO_BACKEND_CC310_HASH_SHA256_ENABLED  - CC310 SHA-256 hash functionality.

// <i> CC310 backend implementation for hardware-accelerated SHA-256.

#ifndef NRF_CRYPTO_BACKEND_CC310_HASH_SHA256_ENABLED
#define NRF_CRYPTO_BACKEND_CC310_HASH_SHA256_ENABLED 1
#endif

// <q> NRF_CRYPTO_BACKEND_CC310_HASH_SHA512_ENABLED  - CC310 SHA-512 hash functionality

// <i> CC310 backend implementation for SHA-512 (in software).

#ifndef NRF_CRYPTO_BACKEND_CC310_HASH_SHA512_ENABLED
#define NRF_CRYPTO_BACKEND_CC310_HASH_SHA512_ENABLED 1
#endif

// <q> NRF_CRYPTO_BACKEND_CC310_HMAC_SHA256_ENABLED  - CC310 HMAC using SHA-256

// <i> CC310 backend implementation for HMAC using hardware-accelerated SHA-256.

#ifndef NRF_CRYPTO_BACKEND_CC310_HMAC_SHA256_ENABLED
#define NRF_CRYPTO_BACKEND_CC310_HMAC_SHA256_ENABLED 1
#endif

// <q> NRF_CRYPTO_BACKEND_CC310_HMAC_SHA512_ENABLED  - CC310 HMAC using SHA-512

// <i> CC310 backend implementation for HMAC using SHA-512 (in software).

#ifndef NRF_CRYPTO_BACKEND_CC310_HMAC_SHA512_ENABLED
#define NRF_CRYPTO_BACKEND_CC310_HMAC_SHA512_ENABLED 1
#endif

// <q> NRF_CRYPTO_BACKEND_CC310_RNG_ENABLED  - Enable RNG support using CC310.

#ifndef NRF_CRYPTO_BACKEND_CC310_RNG_ENABLED
#define NRF_CRYPTO_BACKEND_CC310_RNG_ENABLED 1
#endif

// <q> NRF_CRYPTO_BACKEND_CC310_INTERRUPTS_ENABLED  - Enable Interrupts while support using CC310.

// <i> Select a library version compatible with the configuration. When interrupts are disable, a version named _noint must be used

#ifndef NRF_CRYPTO_BACKEND_CC310_INTERRUPTS_ENABLED
#define NRF_CRYPTO_BACKEND_CC310_INTERRUPTS_ENABLED 1
#endif

// </e>

// <e> NRF_CRYPTO_BACKEND_CIFRA_ENABLED - Enable the Cifra backend.
//==========================================================
#ifndef NRF_CRYPTO_BACKEND_CIFRA_ENABLED
#define NRF_CRYPTO_BACKEND_CIFRA_ENABLED 0
#endif
// <q> NRF_CRYPTO_BACKEND_CIFRA_AES_EAX_ENABLED  - Enable the AES EAX mode using Cifra.

#ifndef NRF_CRYPTO_BACKEND_CIFRA_AES_EAX_ENABLED
#define NRF_CRYPTO_BACKEND_CIFRA_AES_EAX_ENABLED 1
#endif
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

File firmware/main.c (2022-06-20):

/**
 * @file  s1-ecg-demo/main.c
 *
 * @brief Tiny ECG Application running on S1
 *
 *        Includes basic configuration of the S1 module, and
 *        operations required to boot the FPGA. The FPGA
 *        verilog project can be built by running:
 *           "make build-verilog"
 *        from this folder.
 *
 * @attention Copyright 2022 Silicon Witchery AB
 *
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
 * THE SOFTWARE IS PROVIDED "AS IS" AND THE AUTHOR DISCLAIMS
 * ALL WARRANTIES WITH REGARD TO THIS SOFTWARE INCLUDING ALL
 * IMPLIED WARRANTIES OF MERCHANTABILITY AND FITNESS. IN NO
 * EVENT SHALL THE AUTHOR BE LIABLE FOR ANY SPECIAL, DIRECT,
 * INDIRECT, OR CONSEQUENTIAL DAMAGES OR ANY DAMAGES WHATSOEVER
 * RESULTING FROM LOSS OF USE, DATA OR PROFITS, WHETHER IN AN
 * ACTION OF CONTRACT, NEGLIGENCE OR OTHER TORTIOUS ACTION,
 * ARISING OUT OF OR IN CONNECTION WITH THE USE OR PERFORMANCE
 * OF THIS SOFTWARE.
 */

// #define STEPPED_LPM

#include "main.h"

// Globals
static uint16_t fpga_spi_delay_counter = 0;
static nrf_saadc_value_t m_buffer;
static uint8_t SAMPLES_IN_BUFFER = 1;
static uint32_t m_adc_evt_counter;
static int32_t adc_val;

static float buffer[65];
static uint8_t buff_idx = 0;
static uint32_t filtered_val;
static bool ecg_active = 1;

APP_TIMER_DEF(fpga_boot_task_id);
APP_TIMER_DEF(adc_task_id);
APP_TIMER_DEF(filter_task_id);

static fpga_boot_state_t fpga_boot_state = STARTED;
static uint32_t pages_remaining;
static uint32_t page_address = 0x000000;

s1_fpga_pins_t s1_fpga_pins;
static const nrfx_spim_t spi = NRFX_SPIM_INSTANCE(0);

void spi_init()
{
    // SPI hardware configuration
    nrfx_spim_config_t spi_config = NRFX_SPIM_DEFAULT_CONFIG;
    spi_config.mosi_pin = SPI_SO_PIN;
    spi_config.miso_pin = SPI_SI_PIN;
    spi_config.sck_pin = SPI_CLK_PIN;
    spi_config.ss_pin = SPI_CS_PIN;
    spi_config.frequency = NRF_SPIM_FREQ_125K;
    spi_config.ss_active_high = 1; // Inverted CS

    // Initialise the SPI if it was not already
    APP_ERROR_CHECK(nrfx_spim_init(&spi, &spi_config, NULL, NULL));
}

void spi_tx(uint8_t *tx_buffer, uint8_t len)
{
    nrfx_spim_xfer_desc_t spi_xfer = NRFX_SPIM_XFER_TX(tx_buffer, len);
    APP_ERROR_CHECK(nrfx_spim_xfer(&spi, &spi_xfer, 0));
}

void s1_fpga_io_update(s1_fpga_pins_t *s1_fpga_pins)
{
    static uint8_t tx_buffer[2];
    for (int i = 0; i < 8; i++)
    {
        tx_buffer[0] = i; // pin numbering starts at 1
        tx_buffer[1] = s1_fpga_pins->duty_cycle[i];
        spi_tx(tx_buffer, 2);
    }
}

/**
 * @brief Clock event callback. Not used but required to have.
 */
void clock_event_handler(nrfx_clock_evt_type_t event) {}
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

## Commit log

2021-08-10 added schematic
    [s1-ecg-demo.sch]
2021-08-10 added BOM
    [BOM.csv, s1-ecg-demo.sch]
2021-08-12 Updated LEDs and BOM
    [BOM.csv, s1-ecg-demo.sch]
2021-08-13 updated to match eval board
    [BOM.csv, s1-ecg-demo.sch]
2021-08-16 pill shape, nearly done routing
    [BOM.csv, s1-ecg-demo.kicad_pcb, s1-ecg-demo.sch]
2021-08-17 Layout complete, needs checking
    [s1-ecg-demo-B_Cu.gbr, s1-ecg-demo-B_Mask.gbr, s1-ecg-demo-B_SilkS.gbr, s1-ecg-demo-Edge_Cuts.gbr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]
2021-08-18 Final check done
    [s1-ecg-demo-B_Cu.gbr, s1-ecg-demo-B_Mask.gbr, s1-ecg-demo-B_SilkS.gbr, s1-ecg-demo-Edge_Cuts.gbr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]
2021-08-18 end of day 18-08
    [s1-ecg-demo-B_Cu.gbr, s1-ecg-demo-B_Mask.gbr, s1-ecg-demo-B_SilkS.gbr, s1-ecg-demo-Edge_Cuts.gbr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]
2021-08-18 Little bit of clean up fixed battery and current header re-exported gerbers
    [s1-ecg-demo-B_Cu.gbr, s1-ecg-demo-B_Mask.gbr, s1-ecg-demo-B_SilkS.gbr, s1-ecg-demo-Edge_Cuts.gbr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]
2021-08-19 Final files ready for order
    [s1-ecg-demo-B_Cu.gbr, s1-ecg-demo-B_Mask.gbr, s1-ecg-demo-B_SilkS.gbr, s1-ecg-demo-Edge_Cuts.gbr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]
2021-08-19 Simple FIR filter works on ADC data
2021-08-20 1 pin pwm works
2021-08-23 Added factory gerber files
    [c4282frc04a0.drl, c4282frc04a0.gko]
2021-08-26 ecg on led display is ok, auto sdn on leads off
2021-08-31 New BOM added
    [BOM.csv]
2021-09-13 basic low power mode works
2021-10-13 Added shutdown pullup resistor Adjusted current probe header location Updated BOM Exported v2 gerber
    [s1-ecg-demo-B_Cu.gbr, s1-ecg-demo-B_Mask.gbr, s1-ecg-demo-B_SilkS.gbr, s1-ecg-demo-Edge_Cuts.gbr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]
2021-10-13 Fixed ground break Isolation around battery positive terminal Removed the cuttable jumper Cleaned up silkscreen Added 0.1" pin jumper to BOM
    [s1-ecg-demo-B_Cu.gbr, s1-ecg-demo-B_Mask.gbr, s1-ecg-demo-B_SilkS.gbr, s1-ecg-demo-Edge_Cuts.gbr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]
2021-10-15 Updated to latest SDK branch on main Added back fir filter reference image
2021-10-28 added battery spec added factory stencil gerber
    [single-board-top-side-smd-stencil.gbr]
2021-10-28 Uploaded latest production gerber from factory
    [c4282frc04a0.drl, c4282frc04a0.gko, c4282tfc04a0.drl, c4282tfc04a0.gko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]
2022-01-28 Migrated to Kicad 6 Re-exported gerbers with correct WLCSP paste layer
    [s1-ecg-demo-B_Cu.gbr, s1-ecg-demo-B_Mask.gbr, s1-ecg-demo-B_SilkS.gbr, s1-ecg-demo-B_Silkscreen.gbr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]
2022-01-28 Rev 3 PCB Release Only change is the WLCSP solder paste size
    [s1-ecg-demo.kicad_pcb, s1-ecg-demo.kicad_sch]
2022-01-28 Added battery label files
2022-12-12 Replaced licence with CERN OHL-P-v2
    [s1-ecg-demo.kicad_pcb, s1-ecg-demo.kicad_sch]

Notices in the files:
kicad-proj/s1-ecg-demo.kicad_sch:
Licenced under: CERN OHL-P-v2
